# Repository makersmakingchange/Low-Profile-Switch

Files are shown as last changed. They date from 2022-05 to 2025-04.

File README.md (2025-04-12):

# Low-Profile-Switch
A low force hand operated switch

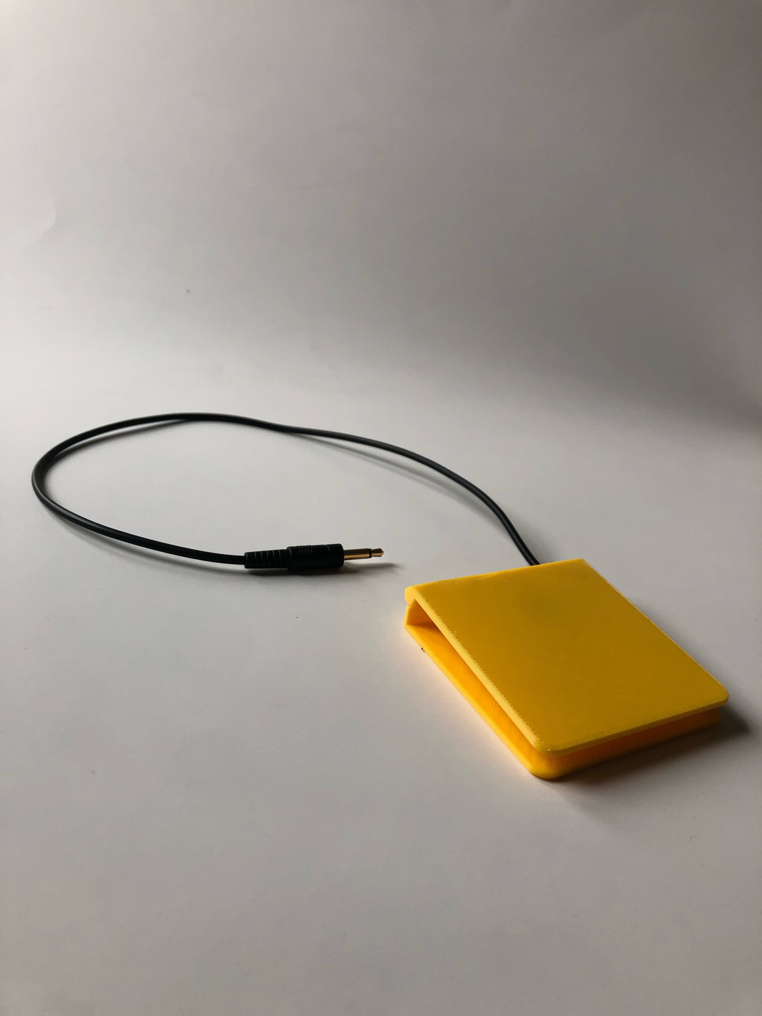
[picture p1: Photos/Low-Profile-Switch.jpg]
Picture of a 3D printed Low Profile Switch.


## More info at
- [Makers Making Change Project Page](https://makersmakingchange.com/project/low-profile-switch/)

## Getting Started
1. How to build this device

All of the files and instructions required to build the Low Profile Switch are contained within this repository. Refer to the Maker Checklist below.

2. How to request a build of this device

If you would like to obtain a Low Profile Switch but do not have the skills or equipment to do so, you may submit a build request through the [MMC Library Page](https://makersmakingchange.com/project/low-profile-switch/). The requestor is responsible for the cost of materials and any shipping.

3. How to build this device for someone else

If you have the skills and equipment to build this device, and would like to donate your time to create the switch for someone who needs it, visit the [MMC Maker Wanted](https://makersmakingchange.com/maker-wanted/) section.

## Files

### Documentation
| Document             | Version | Link                                                                                  |
|----------------------|---------|---------------------------------------------------------------------------------------|
| Maker Checklist      | 1.0     | [Maker Checklist](/Documentation/Low_Profile_Switch_Maker_Checklist_v1.0.pdf)         |
| Bill of Materials    | 1.0     | [BOM](/Documentation/Low_Profile_Switch_BOM_V1.0.xlsx)                                |
| 3D Printing Guide    | 1.0     | [3D Printing Guide](Documentation/Low_Profile_Switch_3D_Printing_Guide_v1.0.pdf)             |
| Assembly Guide       | 1.0     | [Assembly Guide](/Documentation/Low_Profile_Switch_Assembly_Guide_v1.0.pdf)           |      
| User Quick Guide     | 1.0     | [Quick_Guide](/Documentation/Low_Profile_Switch_User_Guide_v1.0.pdf)                  |

## Attribution 

Designed by Kerilyn Kennedy - Makers Making Change.
Documentation created by Neil Squire / Makers Making Change.

## License 
Everything needed or used to design, make, test, or prepare the Low Profile Switch is licensed under the CERN 2.0 Permissive license <https://ohwr.org/project/cernohl/wikis/Documents/CERN-OHL-version-2> (CERN-OHL-P) . 

Accompanying material such as instruction manuals, videos, and other copyrightable works that are useful but not necessary to design, make, test, or prepare the Low Profile Switch are published under a Creative Commons Attribution-ShareAlike 4.0 license <https://creativecommons.org/licenses/by-sa/4.0/> (CC BY-SA 4.0) 

 ----
<!-- ABOUT MMC START -->
## About Makers Making Change
[Makers Making Change Logo](https://www.makersmakingchange.com/)

Makers Making Change is a program of [Neil Squire](https://www.neilsquire.ca/), a Canadian non-profit that uses technology, knowledge, and passion to empower people with disabilities.

Makers Making Change leverages the capacity of community based Makers, Disability Professionals and Volunteers to develop and deliver affordable Open Source Assistive Technologies.

 - Website: [www.MakersMakingChange.com](https://www.makersmakingchange.com/)
 - GitHub: [makersmakingchange](https://github.com/makersmakingchange)
 - Bluesky: [@makersmakingchange.bsky.social](https://bsky.app/profile/makersmakingchange.bsky.social)
 - Instagram: [@makersmakingchange](https://www.instagram.com/makersmakingchange)
 - Facebook: [makersmakechange](https://www.facebook.com/makersmakechange)
 - LinkedIn: [Neil Squire Society](https://www.linkedin.com/company/neil-squire-society/)
 - Thingiverse: [makersmakingchange](https://www.thingiverse.com/makersmakingchange/about)
 - Printables: [MakersMakingChange](https://www.printables.com/@MakersMakingChange)

### Contact Us
For technical questions, to get involved, or to share your experience we encourage you to [visit our website](https://www.makersmakingchange.com/) or [contact us](https://www.makersmakingchange.com/s/contact).
<!-- ABOUT MMC END -->

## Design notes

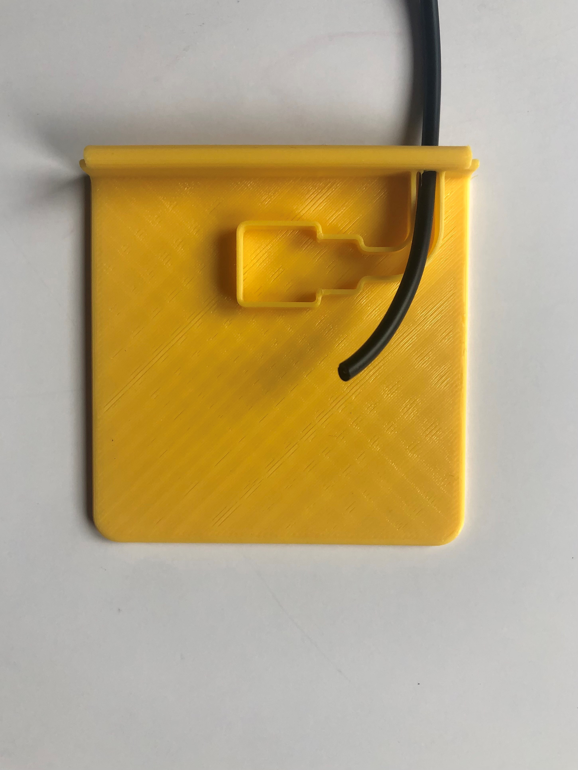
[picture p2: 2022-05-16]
Photos/Low-Profile-Switch_A05.jpg

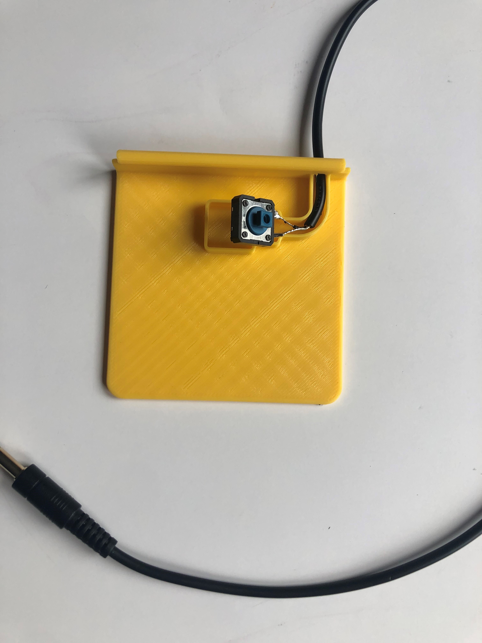
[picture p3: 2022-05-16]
Photos/Low-Profile-Switch_A11.jpg

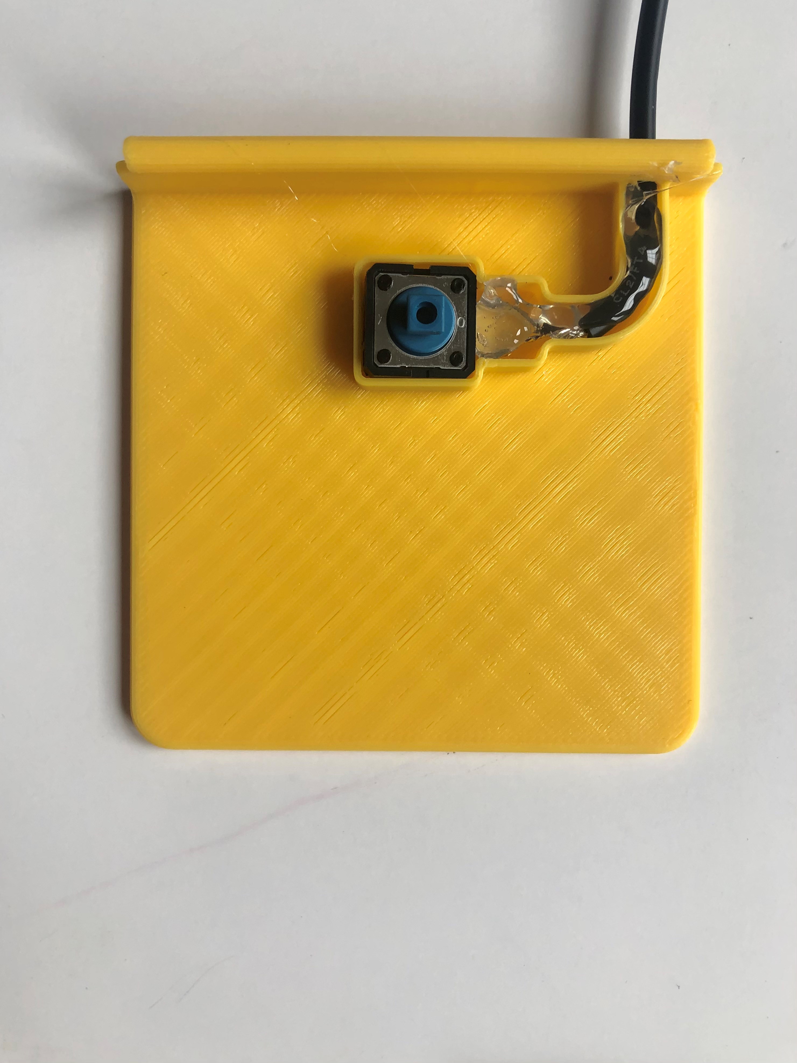
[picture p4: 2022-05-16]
Photos/Low-Profile-Switch_A12.jpg

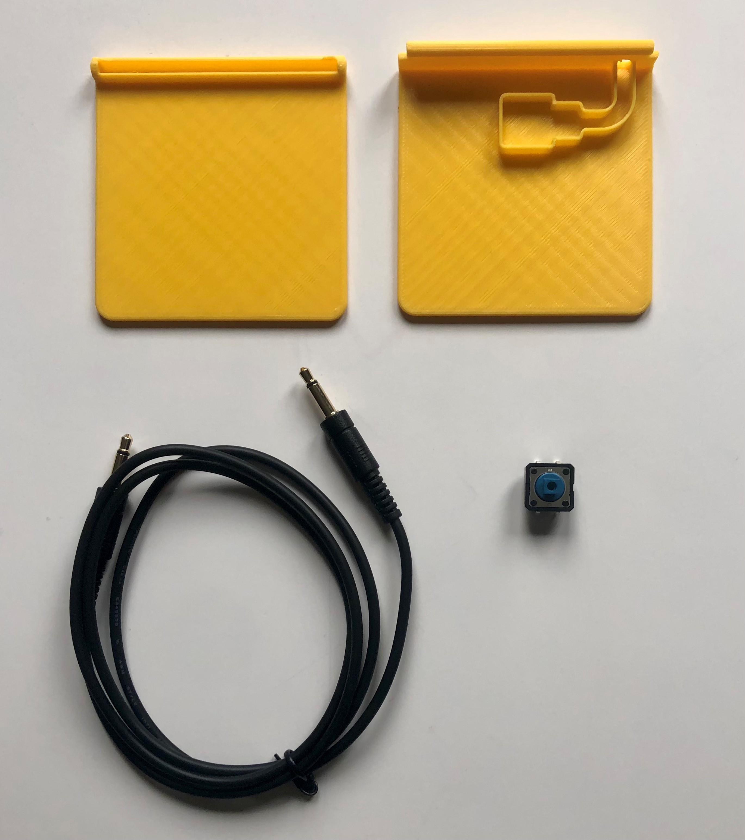
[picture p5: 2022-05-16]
Photos/Low-Profile-Switch_A00.jpg

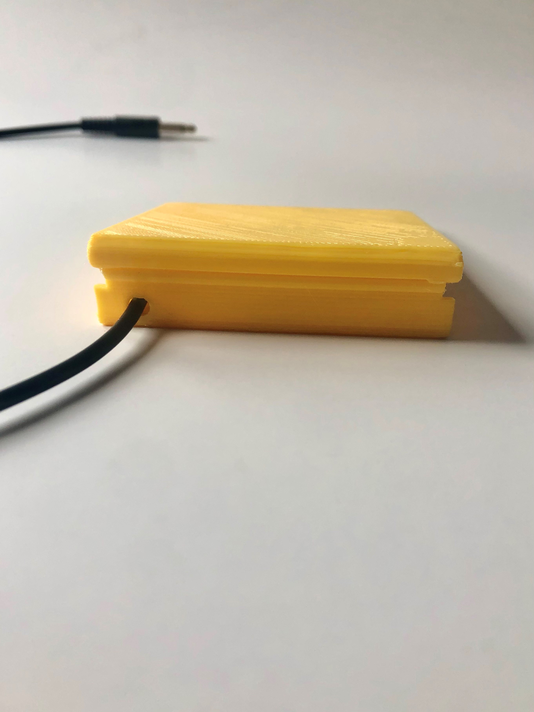
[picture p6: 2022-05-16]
Photos/Low-Profile-Switch_A14.jpg

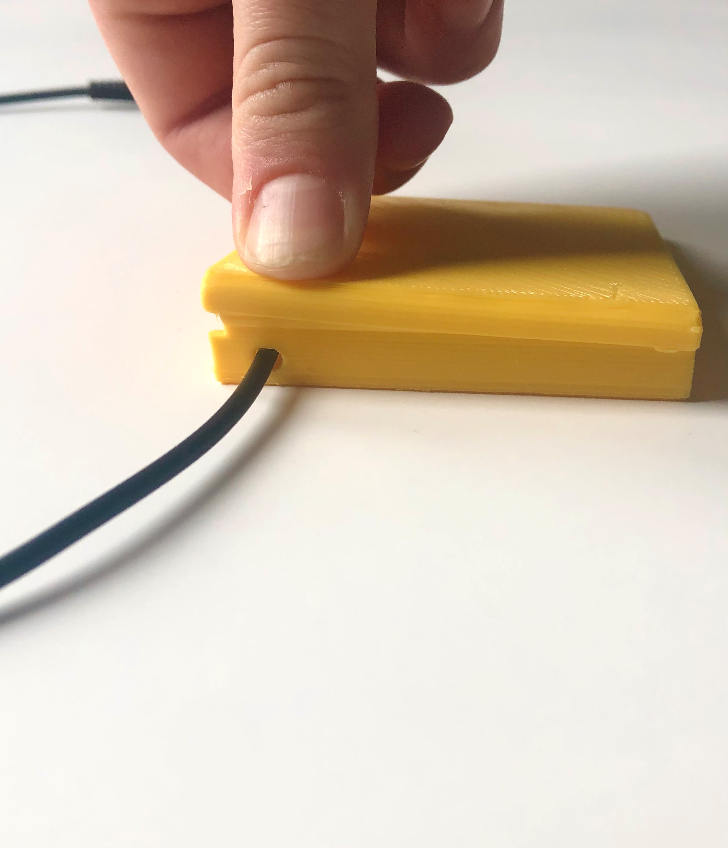
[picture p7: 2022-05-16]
Photos/Low-Profile-Switch_A15.jpg

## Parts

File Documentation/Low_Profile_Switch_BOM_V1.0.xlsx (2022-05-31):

Device: Low Profile Switch |  | Total Cost | Total Print time (hr) | Total filament (g)
Version: V1.0 | Date Created: 5/13/2022 | $6.11 | 1.68 | 23
Commercial Parts:
Part type (Electrical. Mechanical, Sanitization, ect) | Part Number | Quantity Needed | Pkg Quantity | Price per package | Price per Unit | Price for qty needed | Link
3.5 mm mono cable | 839-1039-ND | 1 | 1 | $4.44 | $4.44 | $4.44 | https://www.digikey.ca/short/pt54w9
12 mm tactile switch | SW801-ND | 1 | 1 | $0.98 | $0.98 | $0.98 | https://www.digikey.ca/short/jvzq2d
3D Printed Parts ESTIMATED PRICING USING 1KG ROLL COST: | $30.00
Part | Description | Quantity Needed | TOTAL Mass (g) | Estimated Price | Print Time (Min) | Link
Low_Profile_Switch_Top |  | 1 | 11 | $0.33 | 46
Low_Profile_Switch_Bottom |  | 1 | 12 | $0.36 | 55
 |  |  |  | $0.00
 |  |  |  | $0.00
 |  |  |  | $0.00
 |  |  | Total Print Cost: | $0.69
Tools for Assembly
Soldering Iron
Wire Strippers
Wire Cutters
Hot Glue Gun
Alternatives (if there are other sources for some parts link them below)
Part and description | Link
3.5 mm mono cable | https://www.primecables.ca/p-370665-cab-aud-200-all-35mm-18-inch-mono-ts-male-to-male-28awg-ft4-cable-black?from_pla=google&sku=383506
3.5 mm mono cable - may be found at your local dollar store

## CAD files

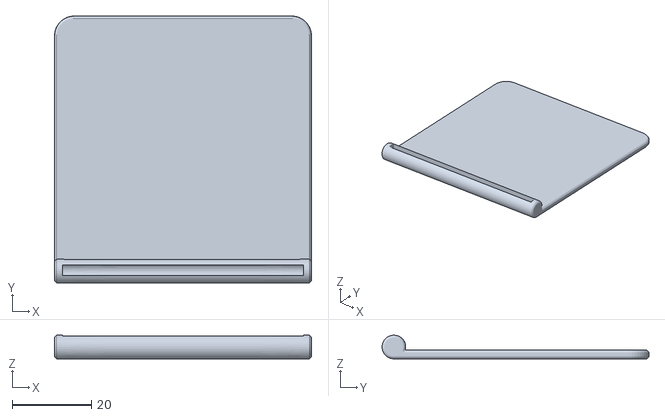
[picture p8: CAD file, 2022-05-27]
Build_Files/Low_Profile_Switch_Top.stl
65.0 x 67.5 x 6.00

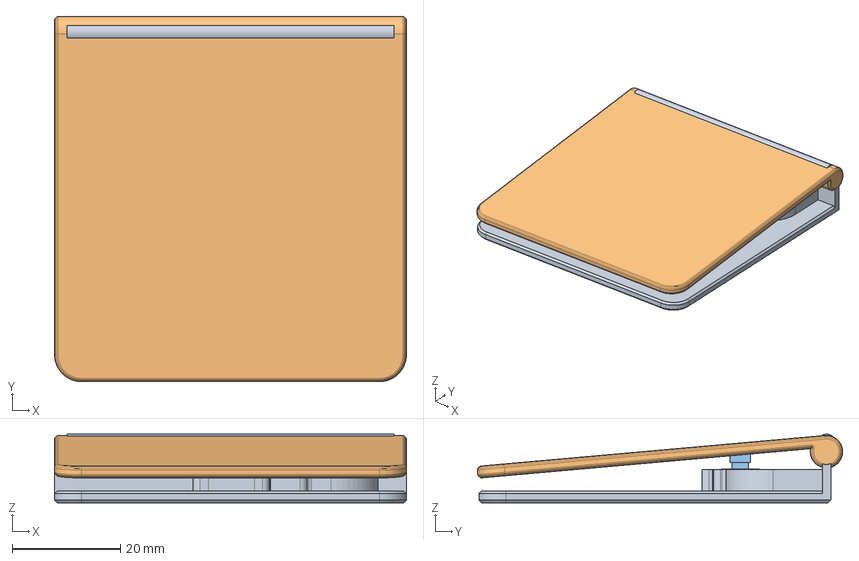
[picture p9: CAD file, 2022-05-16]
Design_Files/Low_Profile_ Switch.step
65.0 x 67.5 x 12.7 mm
Base
Top

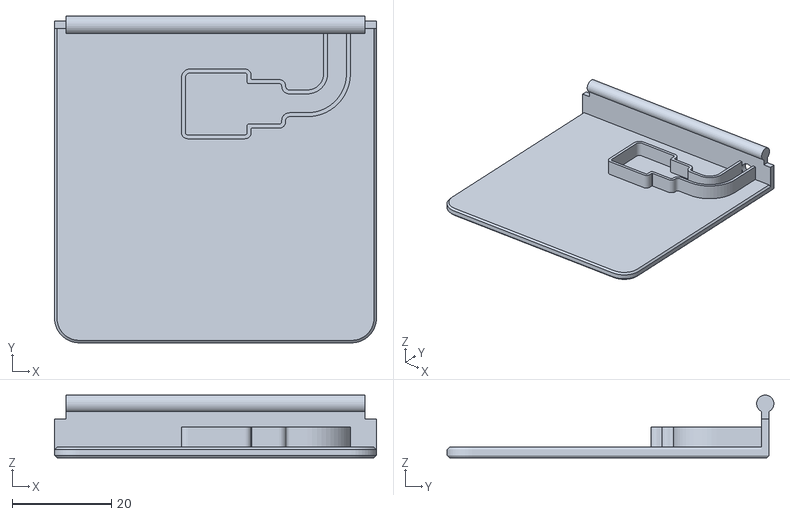
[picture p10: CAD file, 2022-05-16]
Build_Files/Low_Profile_Switch_Bottom.stl
65.0 x 66.0 x 12.7

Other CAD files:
Design_Files/Low_Profile_Switch.dwg

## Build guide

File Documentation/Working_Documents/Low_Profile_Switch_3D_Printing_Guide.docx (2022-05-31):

# 3D Printing Summary

Metrics | Low Profile Switch
Total Print Time (min) | 101
Total Number of Components | 2
Typical Total Mass (g) | 23
Typical Number of Print Setups | 1

# 3D Printing Settings

Print File Name | Qty | Total Print Time (hr:min) | Mass (g) | Infill (%) | Support(Y/N) | Layer Height/ Nozzle Diameter(mm) | Notes (orientation, special settings, etc)
Low_Profile_Switch_Top.stl | 1 | 0:46 | 11 | 20 | N | 0.2/0.4 | The top of the switch must be flat on the print bed.
Low_Profile_Switch_Bottom.stl | 1 | 0:55 | 12 | 20 | N | 0.2/0.4 | Print in orientation given in STL.

# Post-Processing

The Low Profile Switch is printed without supports; hence no post-processing is required.

# Customization Options

The user can request that the device be printed in multiple colours.

# Examples of Quality Prints:

Below is a picture of what quality is expected from printing the device.

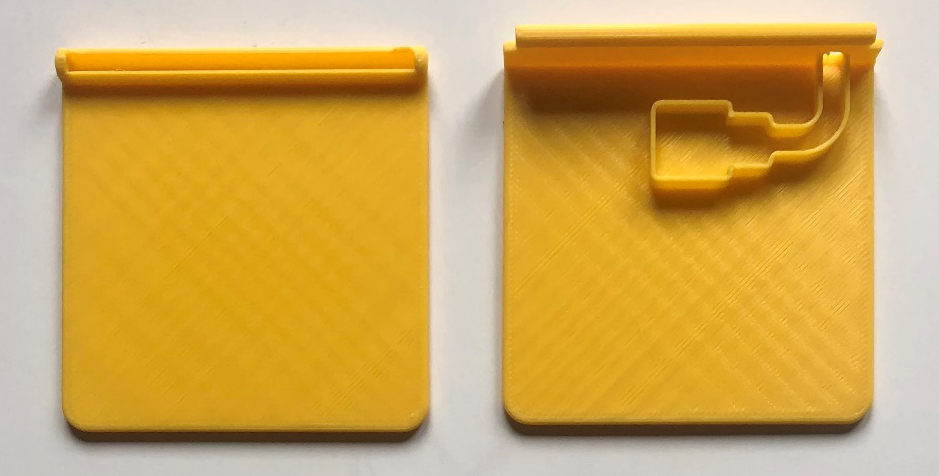
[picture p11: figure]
Picture of good quality prints of the low profile switch top and low profile switch bottom.

© 2022 by Neil Squire / Makers Making Change. This work is licensed under the CC BY SA 4.0 License: http://creativecommons.org/licenses/by-sa/4.0 Files available at https://makersmakingchange.com/project/low-profile-switch/ Page 1 of 2

V1.0 MAY 2022 Low Profile Switch 3D Printing Guide

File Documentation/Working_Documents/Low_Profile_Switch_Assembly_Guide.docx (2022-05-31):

# Required Components

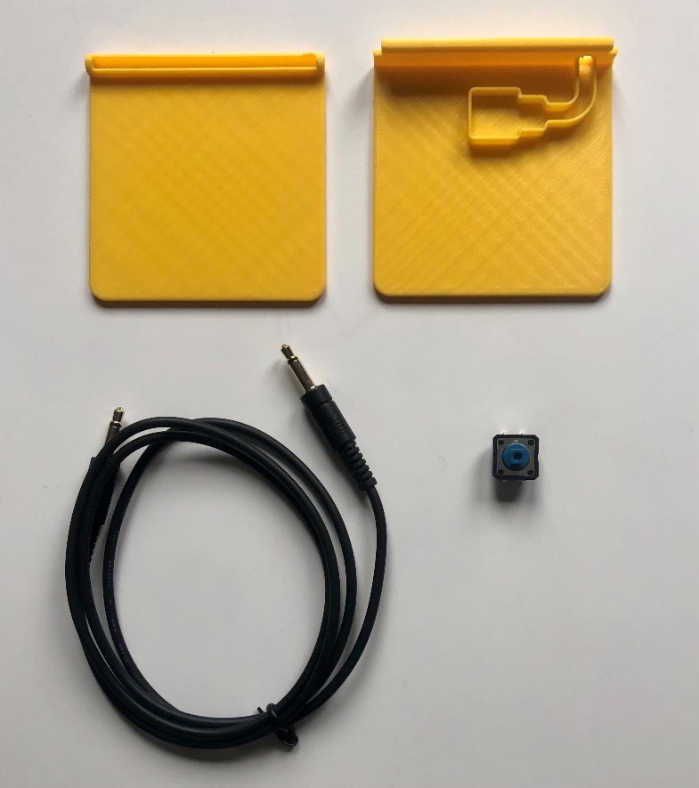
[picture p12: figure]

2 1 4 3 | BILL OF MATERIALS 1x 3D printed switch top 1x 3D printed switch bottom 1x 3.5 mm mono cable 1x 12mm tactile switch 1 4 3 2

# Required Tools

- Soldering Iron and Solder
- Wire Strippers / Wire Cutters
- Hot Glue Gun and Glue

# Required Personal Protective Equipment (PPE)

- Safety Glasses

# Assembly Instructions

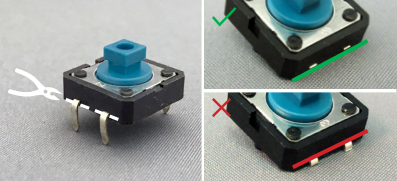
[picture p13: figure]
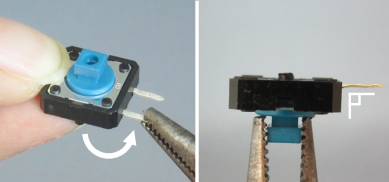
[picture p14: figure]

01. Cut off the two leads on one side flush. | Bend the two remaining leads to make a 90° angle with the switch. 02.

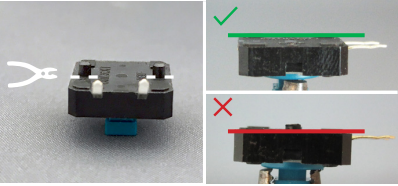
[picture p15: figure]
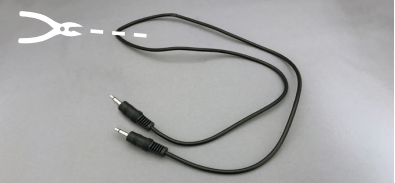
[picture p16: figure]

Cut off the two plastic mounting lugs completely flush. 03. | 04. Cut the mono jack cable to the desired length.

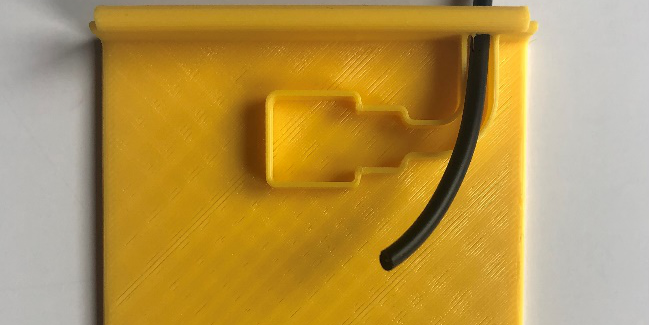
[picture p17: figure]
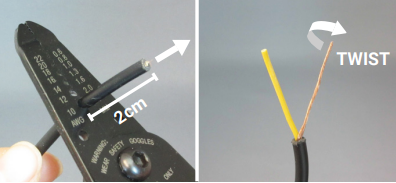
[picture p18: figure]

Pull mono cable through the hole in the base of the switch. 05. | Use the wire strippers to strip 2cm. 06.

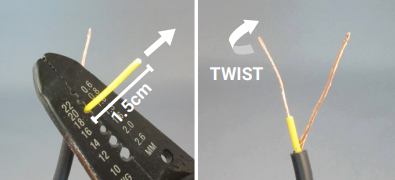
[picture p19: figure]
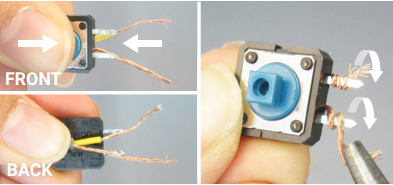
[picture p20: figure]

07. Use wire strippers to strip 1.5cm off the individual wires. | Hold the wire behind the switch and wrap wires around the switch leads. 08.

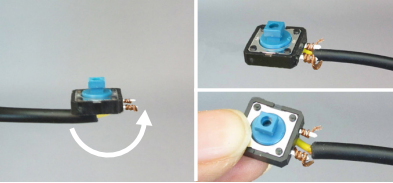
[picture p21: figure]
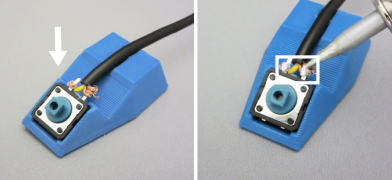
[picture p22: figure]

Hold the switch in place and bend the wire in between the two switch leads. 09. | IMPORTANT: After soldering the two leads indicated in the white rectangle, test the switch by plugging it into a switch tester or assistive device. 10.

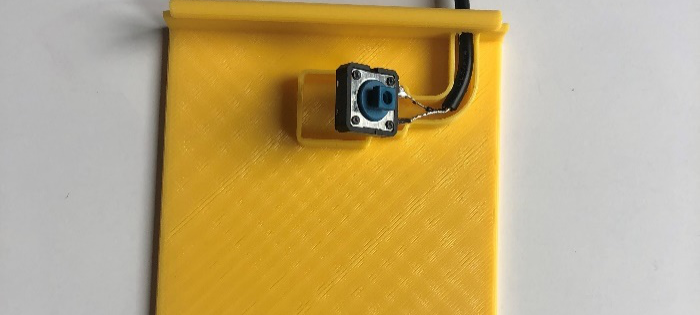
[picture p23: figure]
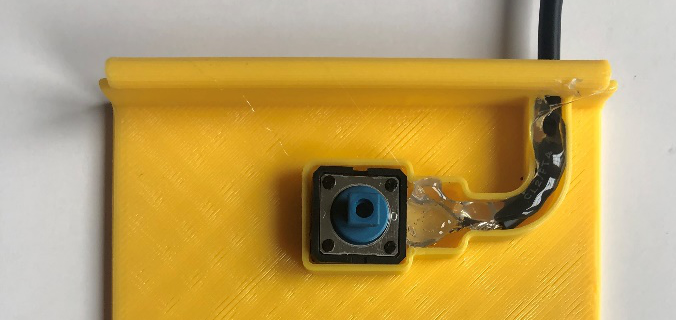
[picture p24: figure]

Move the 3D printed base close to the switch and fit the cable in the 3d printed groove. 11. | Add a small drop of hot glue. Do not add too much. Press down on the switch ensuring that it is sitting level. 12.

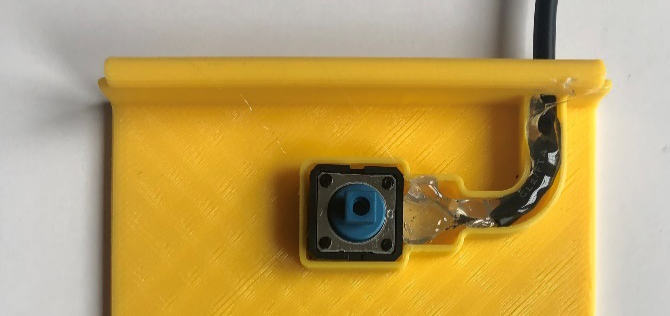
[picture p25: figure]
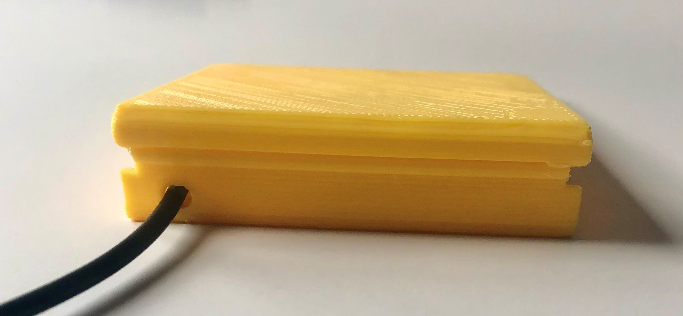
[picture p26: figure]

13. Bury the soldered joint and cable in hot glue. | Place the 3D printed top over the 3D printed base. Align the slot in the top with the joint on the bottom. 14.

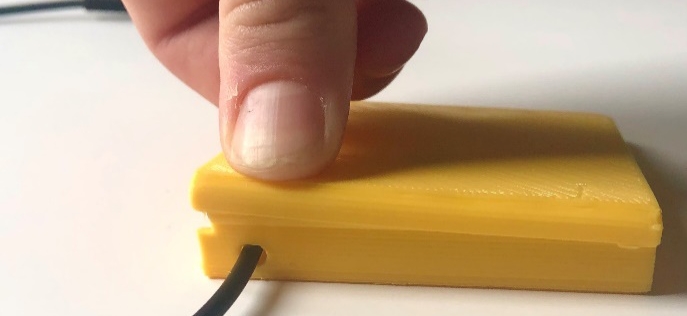
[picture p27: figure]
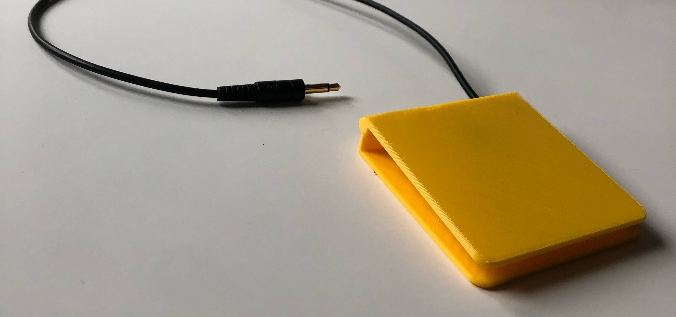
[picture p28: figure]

15. Apply pressure at one end of the top and snap the top onto the base. Then apply pressure to the other end. | 16. Move the top back and forth to insure it is fully snapped on and can rotate freely without friction.

© 2022 by Neil Squire / Makers Making Change This work is licensed under the CC BY SA 4.0 License: http://creativecommons.org/licenses/by-sa/4.0 Files available at https://makersmakingchange.com/project/low-profile-switch/ Page 1 of 1

V1.0 MAY 2022 Low Profile Switch Assembly Guide

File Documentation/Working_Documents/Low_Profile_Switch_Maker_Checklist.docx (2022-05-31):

# Maker To Do List

- Read through the Assembly Guide to become familiar with required components, tools, supplies, and safety gear and overall assembly steps.
- Talk to User about customization options (e.g., color, any special requests, etc.)
- Order switch and monocable.
- Gather tools, supplies, and safety equipment.
- Assemble the device
- Test device
- Print “User Quick Guide”

# Items to Give to User

- Assembled, tested Low Profile Switch
- “User Quick Guide”

© 2022 by Neil Squire / Makers Making Change. This work is licensed under the CC BY SA 4.0 License: http://creativecommons.org/licenses/by-sa/4.0 Files available at https://makersmakingchange.com/project/low-profile-switch/ Page 1 of 1

V1.0 MAY 2022 Low Profile Switch Maker Checklist

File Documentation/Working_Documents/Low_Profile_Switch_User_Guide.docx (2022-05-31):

## Introduction

This is a cost-effective 3D printable accessibility switch that only requires the user to lift their finger or hand as high as 8 mm to use it. The switch measures 65 mm L x 65 mm W x 13 mm H and is built using a standard 3.5 mm cable. Using the specified model of tactile switch, the activation force to use the switch is low and is comparable to the force required to activate the light touch switch.

## Usage

The switch is well-suited for use by a finger or hand. This switch would be beneficial for someone who may have a limited range of motion and would benefit from using a switch that has a large activation area with a minimum switch height. This switch can be plugged into any standard AT interface that uses a 3.5mm cables, including the Xbox Adaptive Controller (XAC).

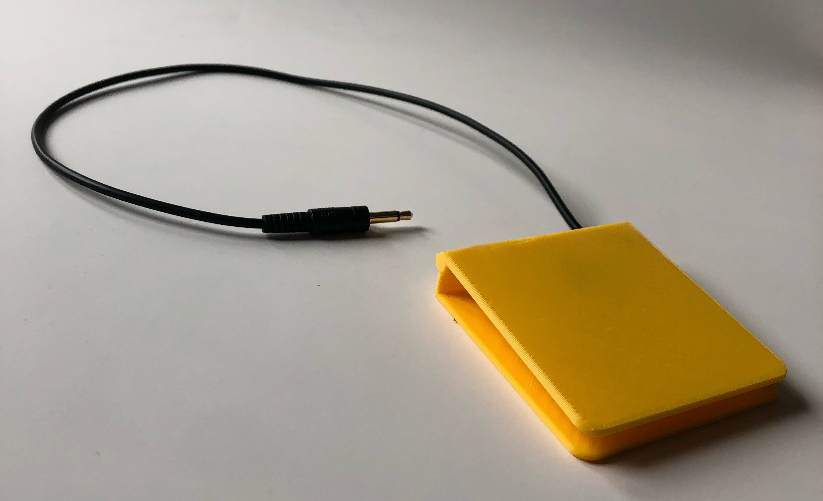
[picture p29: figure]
3D printed low profile switch

## Compatibility

The switch can be plugged into any standard assistive technology interface that uses a 3.5 mm cable.

## Specifications

Length (mm) | Width (mm) | Height (mm) | Mass (g)
65 | 65 | 8 | 23

## Cleaning

The Low Profile Switch can be wiped down with sanitizing cleaners. Do not wash the Low Profile Switch in high heat as it may cause it to melt or break. (i.e., do not put it in the dishwasher, the washing machine, or soak it in hot water).

© 2022 by Neil Squire. This work is licensed under the CC BY SA 4.0 License: http://creativecommons.org/licenses/by-sa/4.0 Files available at https://makersmakingchange.com/project/low-profile-switch/ Page 2 of 3

V1.0 | MAY 2022 Low Profile Switch user Quick Guide

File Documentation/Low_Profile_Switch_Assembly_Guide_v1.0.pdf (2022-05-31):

V1.0 MAY 2022

## Low Profile Switch

## ASSEMBLY GUIDE

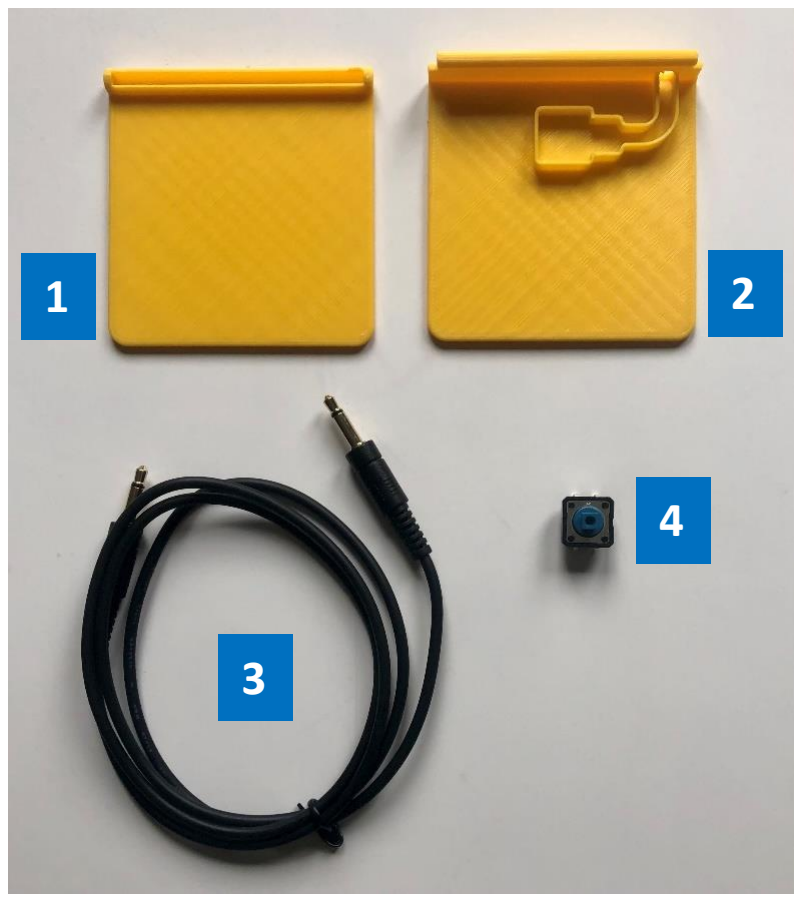
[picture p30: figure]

© 2022 by Neil Squire / Makers Making Change This work is licensed under the CC BY SA 4.0 License: http://creativecommons.org/licenses/by-sa/4.0
Files available at https://makersmakingchange.com/project/low-profile-switch/ | Page 1 of 3

### Required Components

BILL OF MATERIALS

### Required Tools

- Soldering Iron and Solder
- Wire Strippers / Wire Cutters
- Hot Glue Gun and Glue

### Required Personal Protective Equipment (PPE)

- Safety Glasses

1x 3D printed switch top

1x 3D printed switch bottom

1x 3.5 mm mono cable

1x 12mm tactile switch

1

2

3

4

## ASSEMBLY GUIDE

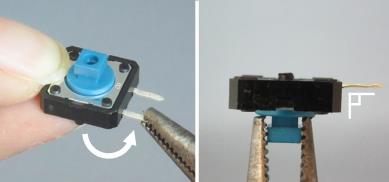
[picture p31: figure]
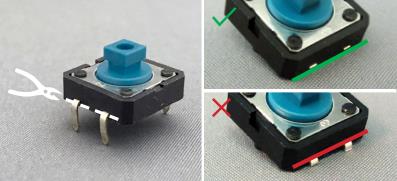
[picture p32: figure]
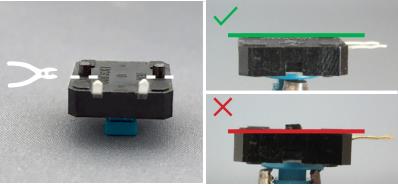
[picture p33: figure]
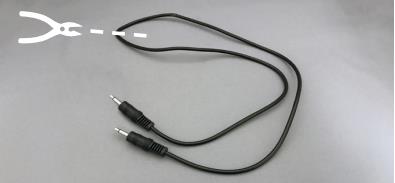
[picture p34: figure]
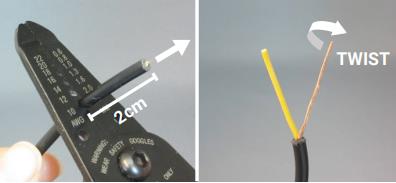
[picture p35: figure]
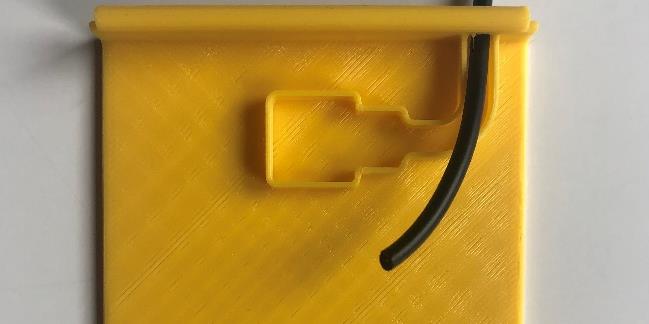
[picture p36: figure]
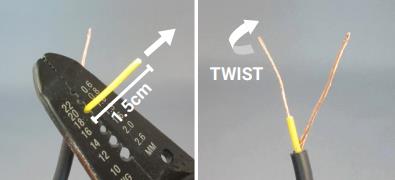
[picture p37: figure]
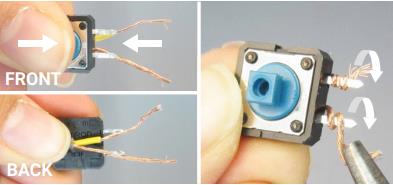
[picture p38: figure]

Files available at https://makersmakingchange.com/project/low-profile-switch/ | Page 2 of 3

### Assembly Instructions

01. 02.
03. 04.
05. 06.
07. 08.

Cut off the two leads on one side flush.

Bend the two remaining leads to make a 90° angle with the switch.

Cut off the two plastic mounting lugs completely flush.

Cut the mono jack cable to the desired length.

Pull mono cable through the hole in the base of the switch.

Use the wire strippers to strip 2cm.

Use wire strippers to strip 1.5cm off the individual wires.

Hold the wire behind the switch and wrap wires around the switch leads.

## ASSEMBLY GUIDE

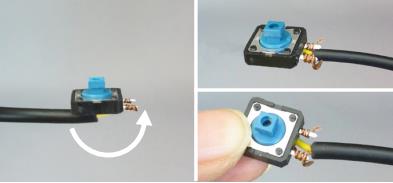
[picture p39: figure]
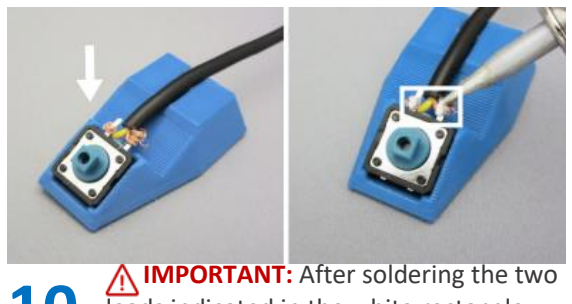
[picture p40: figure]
IMPORTANT: After soldering the two
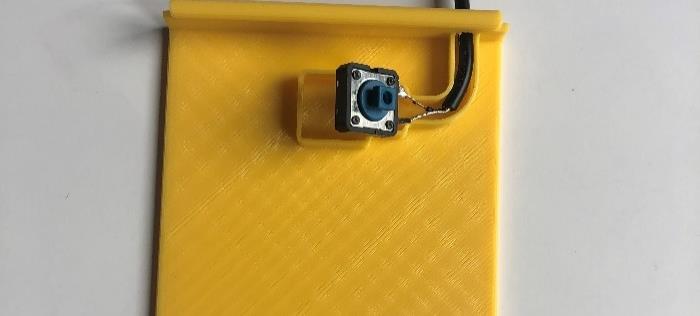
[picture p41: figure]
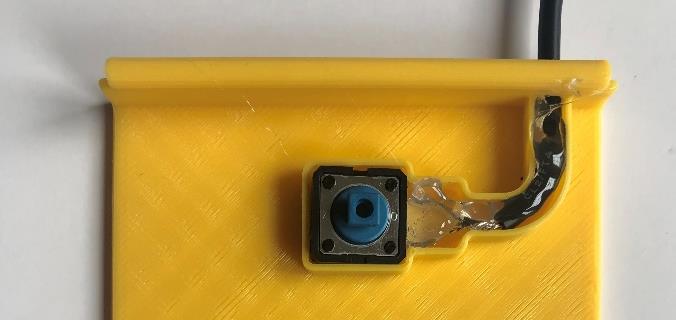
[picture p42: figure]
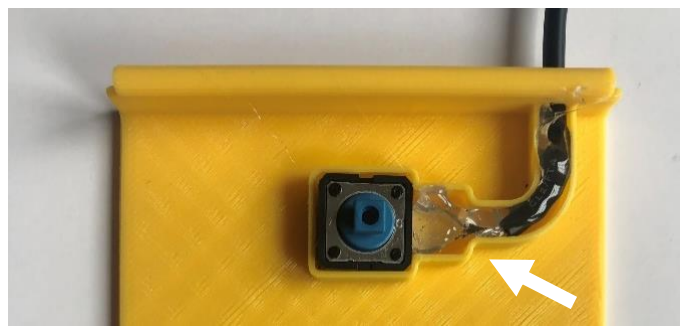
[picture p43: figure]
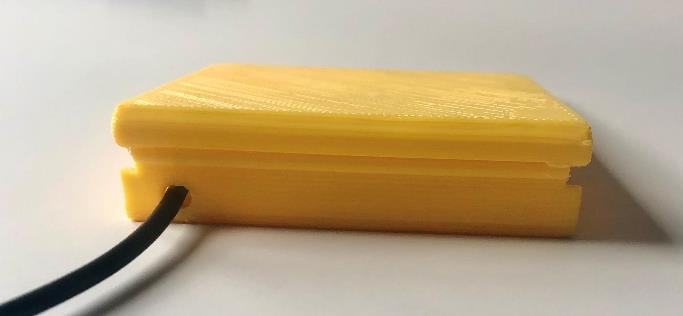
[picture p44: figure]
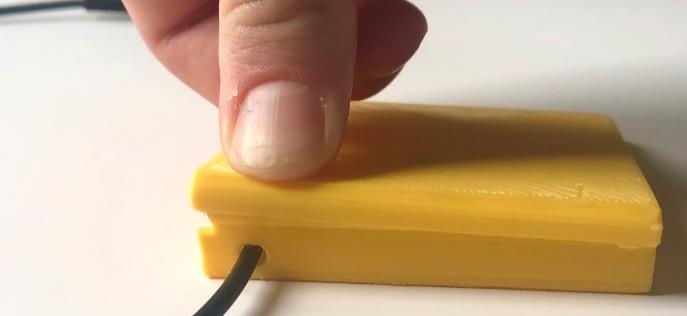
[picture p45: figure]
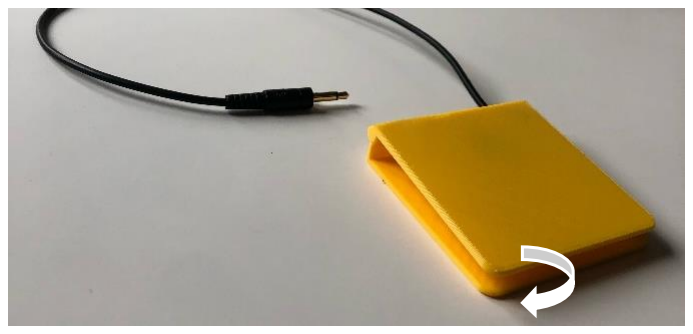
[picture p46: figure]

Files available at https://makersmakingchange.com/project/low-profile-switch/ | Page 3 of 3
09. 10.
11. 12.
13. 14.
15. 16.

Hold the switch in place and bend the wire in between the two switch leads.

leads indicated in the white rectangle, test the switch by plugging it into a switch tester or assistive device.

Move the 3D printed base close to the switch and fit the cable in the 3d printed groove.

Add a small drop of hot glue. Do not add too much. Press down on the switch ensuring that it is sitting level.

Bury the soldered joint and cable in hot glue.

Place the 3D printed top over the 3D printed base. Align the slot in the top with the joint on the bottom.

Apply pressure at one end of the top and snap the top onto the base. Then apply pressure to the other end.

Move the top back and forth to insure it is fully snapped on and can rotate freely without friction.

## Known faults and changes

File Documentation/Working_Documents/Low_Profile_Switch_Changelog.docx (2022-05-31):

# Version 1.0 | Date 05/13/2022

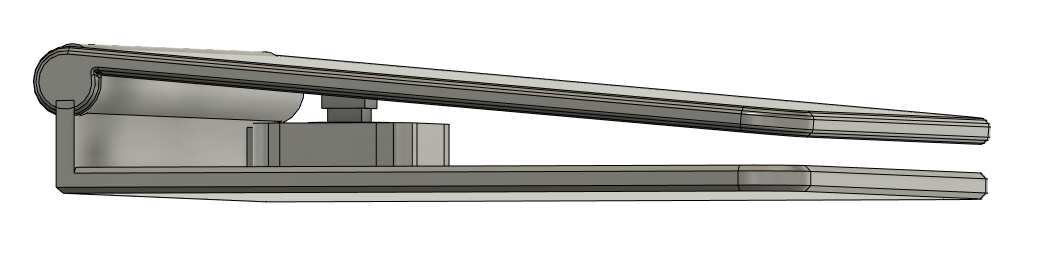
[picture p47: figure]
Screenshot showing side view of Low Profile Switch CAD model

- Initial version
- Designed by Kerilyn Kennedy – Makers Making Change
- Documentation by Neil Squire/Makers Making Change

© 2022 by Neil Squire / Makers Making Change. This work is licensed under the CC BY SA 4.0 License: http://creativecommons.org/licenses/by-sa/4.0 Files available at https://makersmakingchange.com/project/low-profile-switch/ Page 1 of 1

V1.0 MAY 2022 Low Profile Switch changelog

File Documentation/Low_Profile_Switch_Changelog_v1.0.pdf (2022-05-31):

V1.0 MAY 2022

# Low Profile Switch

# CHANGELOG

© 2022 by Neil Squire / Makers Making Change. This work is licensed under the CC BY SA 4.0 License: http://creativecommons.org/licenses/by-sa/4.0
Files available at https://makersmakingchange.com/project/low-profile-switch/ | Page 1 of 1

# Version 1.0 | Date 05/13/2022

## - Initial version - Designed by Kerilyn Kennedy – Makers Making Change - Documentation by Neil Squire/Makers Making Change
